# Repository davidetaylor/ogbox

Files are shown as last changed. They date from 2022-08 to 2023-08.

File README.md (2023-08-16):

# ogbox
Pattern generator for optogenetic experiments. 

## Build instructions

1. Print case and assemble electronics based on wiring diagram.
2. Label the BNCs as "Trigger IN" and "Voltage OUT"
3. Connect the OGBox to computer via USB. Next, install the Adafruit_MCP4725 library by copying it from "firmware/libraries" to the Arduino "libraries" folder on your computer (on Windows this is C:Users\%USERNAME%\Documents\Arduino\libraries). Finally, compile and upload the firmware sketch (OGBox.ino) using the Arduino IDE.
4. You can verify that the OGBox is working correctly by connecting the output to an oscilloscope or LED driver and setting the toggle switch to PREVIEW mode. The default pattern should be a 1Hz pulse. (Note: if you don't see anything initially, the toggle switch might be set to TRIGGERED mode instead of PREVIEW mode).

| Part  | Source |  Quantity |
| ---  | --- |  --- |
| Arduino Micro  | https://www.digikey.com/en/products/detail/arduino/A000053/4486332  |  1  |
| MCP4725 12Bit DAC  | https://www.digikey.com/en/products/detail/adafruit-industries-llc/935/4990759 |  1  |
| Toggle switch  | https://www.digikey.com/en/products/detail/e-switch/100SP1T1B1M2QEH/378821  |  1  |
| Half sized solderless breadboard | https://www.digikey.com/en/products/detail/adafruit-industries-llc/64/7241427  |  1  |
| Female BNC leads | https://www.digikey.com/en/products/detail/pomona-electronics/4969/603340  |  2  |
| Case | 3D printed  |  1  |

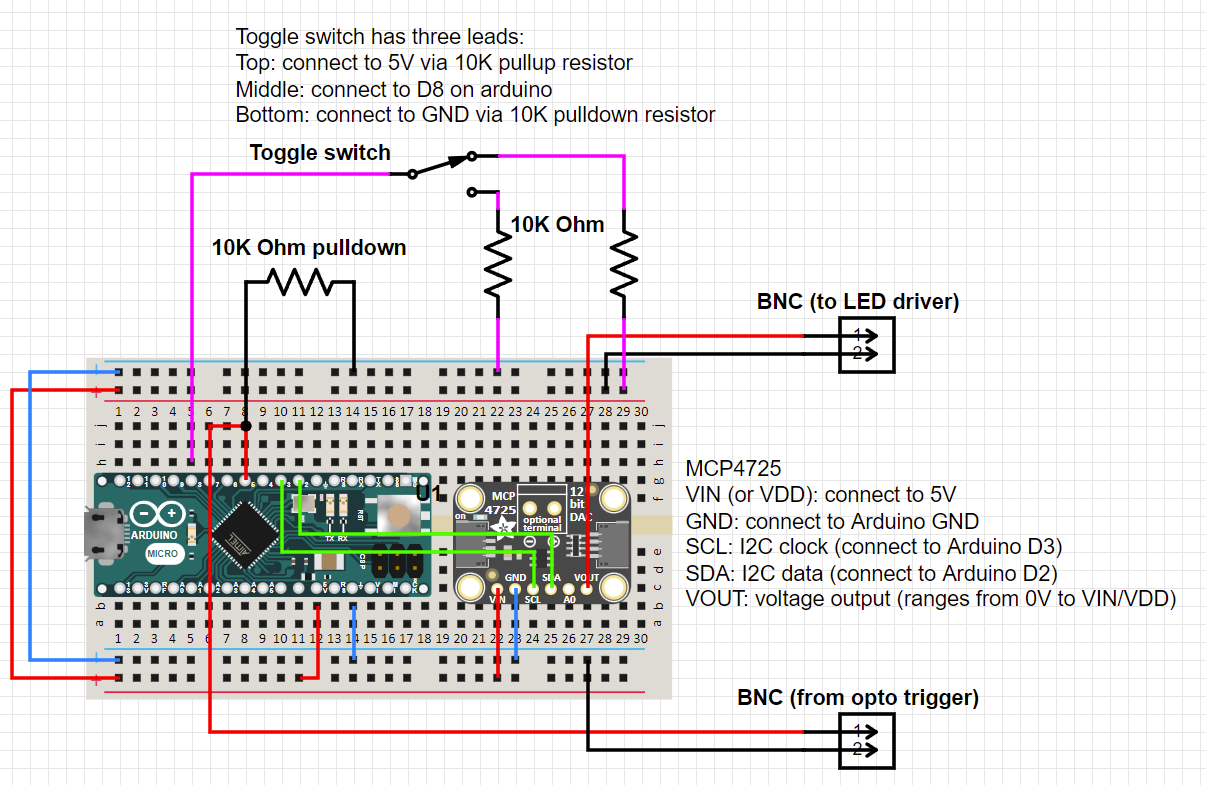
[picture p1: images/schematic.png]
OGBox wiring diagram

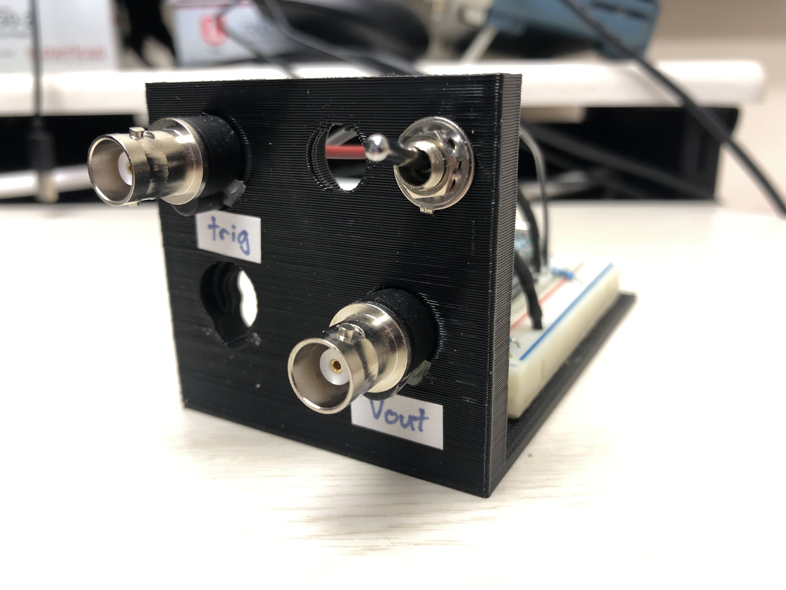
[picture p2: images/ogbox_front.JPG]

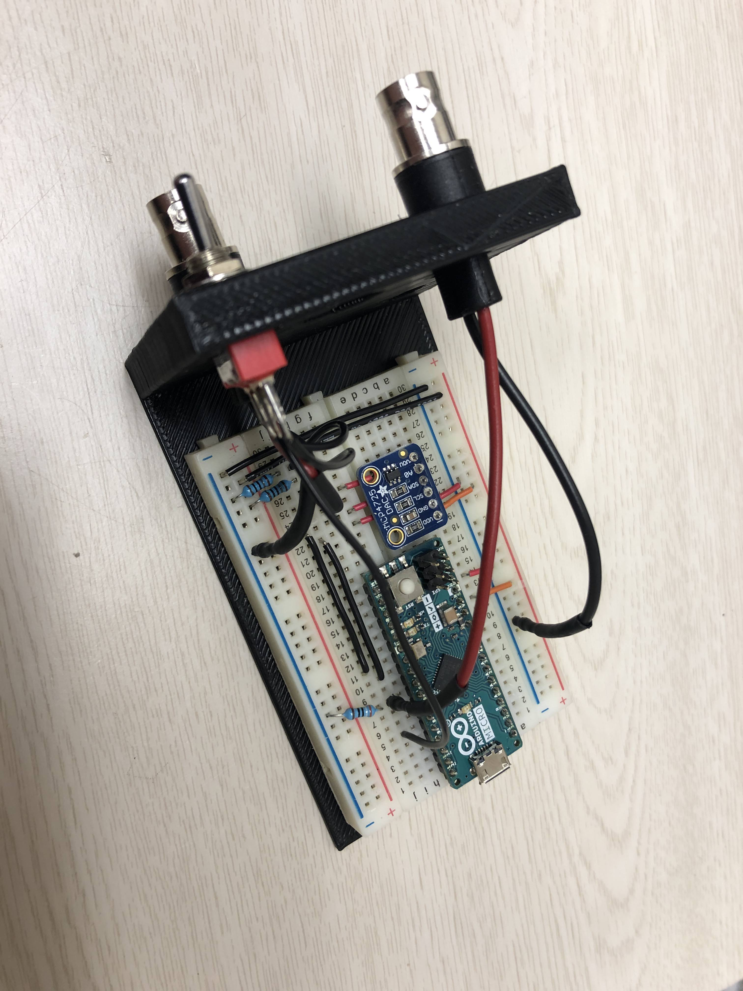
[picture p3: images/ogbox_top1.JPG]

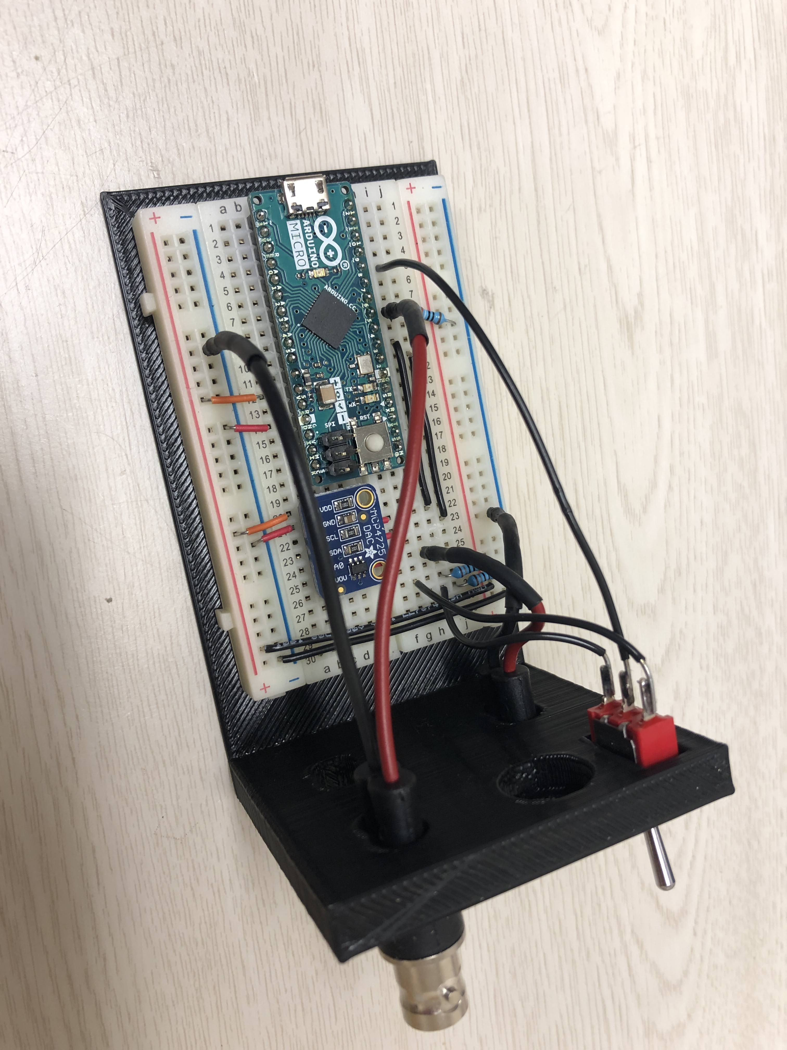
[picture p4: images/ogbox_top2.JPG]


## Integrating OGBox into setup

### Overview
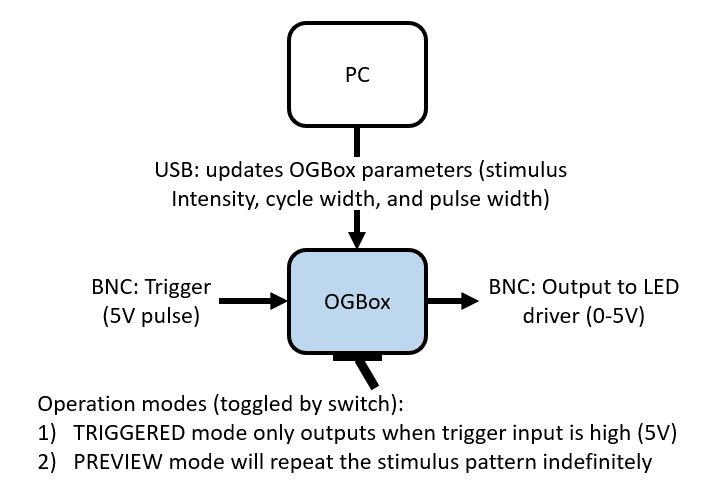
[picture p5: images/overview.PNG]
Overview


### Step-by-step
1. The OGBox is used to operate [Thorlabs T-Cubes](https://www.thorlabs.com/newgrouppage9.cfm?objectgroup_id=2616) which are set to Modulation Mode (i.e., the cube output current exactly follows the amplitude and waveform of the voltage input signal independent from the knob setting). Connect the output of the OGBox to the T-Cube "MOD IN" with a BNC cable.
2. There are two different operation modes for the OGBox: TRIGGERED and PREVIEW modes. In TRIGGERED mode the OGBox will only output while the Trigger Input is high (5V). In PREVIEW mode, the stimulus pattern will repeat indefinitely.
3. The OGBox generates patterned waveforms based on three parameters: Intensity, Cyclelength, and Pulselength. These parameters are set via the USB connection with the Behavioral Control PC. The code in "matlab/demo.m" explains how to change OGBox parameters.
    - Intensity (ranges from 0-4095 and is proportional to maximum power output of the LED)
    - Cyclelength (time between pulses in milliseconds). Stimulus will be constant if set to 0.
    - Pulselength (length of each pulse in milliseconds). Stimulus will be constant if set to 0.
4. When the OGBox is in TRIGGERED Mode, it will only output a voltage pattern while the Trigger Input is high (5V). We use another Arduino to control the timing of all experimental components, so that provides the trigger signal for the OGBox.

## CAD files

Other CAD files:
hardware/ogbox_case.skp

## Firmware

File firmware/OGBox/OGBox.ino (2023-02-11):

#include <Adafruit_MCP4725.h>

// Pin definitions
#define TRIGGER_PIN 5
#define STIM_MODE_PIN 8   // TRIGGERED mode = LOW, PREVIEW mode = HIGH
#define DEBUG_LED_PIN 13
// PIN 2: Reserved for Adafruit_MCP4725 i2c SDA 
// PIN 3: Reserved for Adafruit_MCP4725 i2c SCL

Adafruit_MCP4725 dac;

// ====== STATE VARIABLES ======
bool NEW_COMMAND = false;
int TRIGGER_STATE = LOW;
int STIM_MODE = LOW;

// Timing variables
unsigned long cycleStartTime = 0;
unsigned long pulseStartTime = 0;
unsigned long currentTime = micros();

// Stimulus parameters
String current_line;

int opto_INTENSITY = 1000;
int opto_CYCLELENGTH = 1000;
int opto_PULSELENGTH = 500;

long opto_CYCLELENGTH_MICROS = long(opto_CYCLELENGTH)*1000;
long opto_PULSELENGTH_MICROS = long(opto_PULSELENGTH)*1000;

void setup()
{

  // Connect to Adafruit_MCP4725
  dac.begin(0x62);
  
  pinMode(TRIGGER_PIN, INPUT);
  pinMode(STIM_MODE_PIN, INPUT);
  Serial.begin(9600);           // start serial for output
}

void loop() {

  if (Serial.available() > 0) {

    // PARSE COMMAND STRING FROM BEHAVIOR COMPUTER
    current_line = Serial.readStringUntil(',');
    opto_INTENSITY = current_line.toInt();
    current_line = Serial.readStringUntil(',');
    opto_CYCLELENGTH = current_line.toInt();
    opto_CYCLELENGTH_MICROS = long(opto_CYCLELENGTH)*1000;
    current_line = Serial.readStringUntil('\n');
    opto_PULSELENGTH = current_line.toInt();
    opto_PULSELENGTH_MICROS = long(opto_PULSELENGTH)*1000;

    NEW_COMMAND = 1;
  }

  STIM_MODE = digitalRead(STIM_MODE_PIN);
  if (STIM_MODE == LOW) {
    TRIGGER_STATE = digitalRead(TRIGGER_PIN);
  }
  else {
    TRIGGER_STATE = HIGH;
  }

  if (TRIGGER_STATE == HIGH) {
    // Constant stimulus
    if (opto_CYCLELENGTH_MICROS == 0 | opto_PULSELENGTH_MICROS == 0) {
      dac.setVoltage(opto_INTENSITY, false);
    }
    // Pulsed stimulus
    else {
      unsigned long currentTime = micros();
      if ((currentTime-cycleStartTime) >= opto_CYCLELENGTH_MICROS) {
        cycleStartTime = currentTime;
        pulseStartTime = cycleStartTime;
        dac.setVoltage(opto_INTENSITY, false);
        digitalWrite(DEBUG_LED_PIN, HIGH);
      }
      if ((currentTime-pulseStartTime) >= opto_PULSELENGTH_MICROS) {
        dac.setVoltage(0, false);
        digitalWrite(DEBUG_LED_PIN, LOW);
      }
    }
  }

  // Stimulus off
  else {
    dac.setVoltage(0, false);
    digitalWrite(DEBUG_LED_PIN, LOW);
  }
}

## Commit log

2023-02-11 moved arduino code to 'firmware' folder and added DAC library
2023-02-11 added hardware directory to store 3d models
    [ogbox_case.skp]
